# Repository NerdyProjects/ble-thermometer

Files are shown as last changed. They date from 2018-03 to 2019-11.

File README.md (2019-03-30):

# Bluetooth Low Energy Thermometer

This project describes a bluetooth low energy thermometer.

All code licenced as GPLv3, all documentation and PCB as CC0.

## Purpose
### Conceptual idea: fertility awareness method thermometer

The fertility awareness method, especially the symptothermal method, is a method to classify a woman's fertility by carefully monitoring symptoms of the body to be able to know in which state of the menstrual cycle she is.
One of the monitored symptoms is the body temperature:
The fundamental body temperature is normally taken early in the morning, directly after waking up after a restful sleep.
Women using this method, mostly use a clinical thermometer that has two digits, so a resolution of 0.01 °C.
To get an accurate measurement, measuring inside the vagina or the anus for at least 2 minutes is strongly recommended.
Because of practical reason, most chose to measure inside the vagina.

As a fan of natural birth control, I wanted to support woman by providing a device that relieves them of some stress of the temperature measurement as well as provides additional, maybe interesting data:
  * Not having to think about measuring the temperature in the morning
  * Not having to set an alarm for the same time (for some people the measurement time has a strong influence on the temperature, so you should always measure at a similar time)
  * Being able to detect factors that change your temperature more easily
  * Maybe even providing a better safety of the method by providing more data
  * Not having to immediately write down the measurement result

So the idea was born:
A thermometer, 
  * that can be inserted into the vagina
    * over night
    * the whole day
    * maybe even just in the early morning for some minutes
  * that records and stores the temperature
  * that can be read out using a smartphone or a computer
  * where there is high value on the ease of use as well as user privacy (no cloud service)
  * that does not hide the complexity of the symptothermal method (e.g. ONLY a thermometer, not a full birth control solution)

Initially, I wrote down more thoughts in a [design.md](design document) which is very far from how reality evolved.

I decided to go for the following system design:
  * Battery powered device powered by the ST SPBTLE-1S Bluetooth low Energy System-on-Chip application processor
  * Bosch BMP280 temperature/pressure sensor (because its high accuracy, low power usage, ease of use and my experience with it)
  * BR1632 lithium coin cell (because of availability as high temperature device)
  * altogether put on a small pcb surrounded by silicone to be completely safe to be used in contact with skin or mucous membrane

This design has a few limitations that are clear even before the first prototype has been built:
  * Limited battery lifetime: Device becomes unusable after ~1-3 years
    * Battery can be exchanged by replacing the silicone
  * High price: Pure materials cost ~15 € per piece
  * Silicone mould might need fiddling a bit

## Prototype
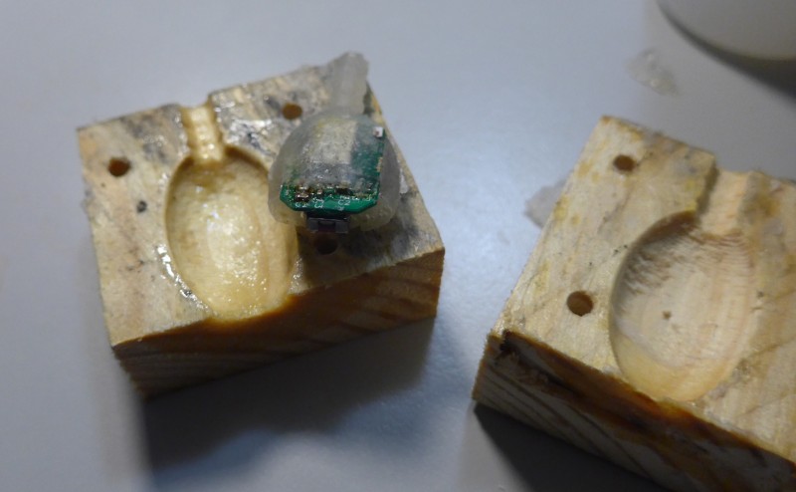
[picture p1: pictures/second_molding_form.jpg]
first mould form and a non-working prototype

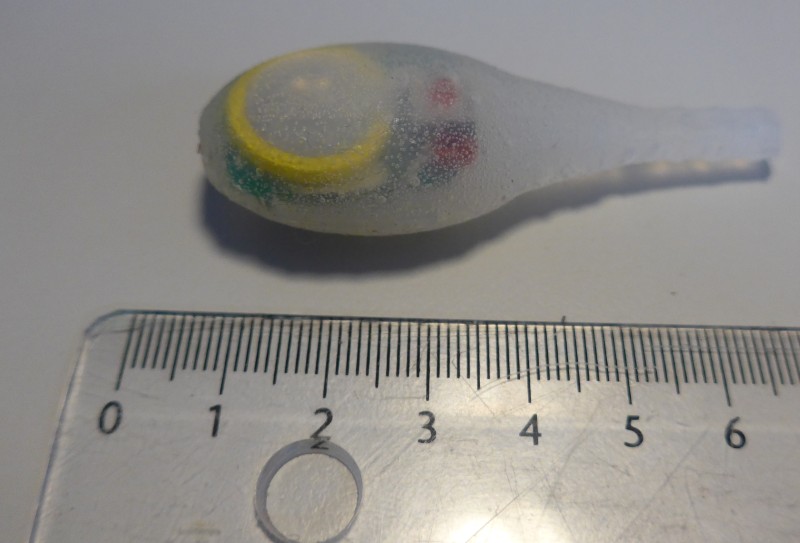
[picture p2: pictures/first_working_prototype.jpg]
first working prototype with refined form


## System architecture
The SPBTLE-1S is a System-on-Chip including a Cortex M0 processor, some flash and Ram, typical microcontroller peripherals and a bluetooth low energy radio.
The bluetooth low energy radio comes with a proprietary, binary-only library, that is linked to the custom user program and provides high level methods to configure the bluetooth part of the device as well as transfer data.

Different libraries are provided by ST that allow creating a running application easily.

The device contains two softwares:
  * The OTA Service Manager, which openly listens for bluetooth connections to reprogram the firmware. It is started after powerup and automatically boots the application software after some seconds.
  * The actual application software. It implements a "safety feature" Long pressing the button (for > 25 seconds) resets the chip, starting in the OTA Service Manager.

## Theory of operation
The thermometer device has different operating modes, whereby it should be kept in mind that the device itself can never be completely powered off.

  * Standby: Time-tracking mode, just counts how long in the past the last measurement has been taken. Can be woken up by button press.
  * Recording: The device takes a measurement point in a fixed (but configurable) interval. Up to 4096 points can be stored before the oldest one gets overwritten.
  * Connectable: The device advertises its Bluetooth low Energy services and is connectable by a paired device. As this mode takes quite some power, it should only be active for a short time.
  * Connected: The device is connected to another device. Data can be read out, configuration can be changed. This mode also takes a bit more power and should only be active for a short time.
  * Pairable: The device advertises its services and is connectable and pairable by other devices.

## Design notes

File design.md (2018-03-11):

# Description

This project describes a thermometer, that should be able to measure temperatures in intervals over a certain time span.
It should be small, self-powered, reusable and easy to be used.
Its designed purpose is especially for fertility awareness methods but also for general sports and medical purposes.
Therefore, it should fulfil the following criteria:

* Small in size to be inserted into the vagina for some period of time
  * Ideally, also swalloable if possible in size
* Safe to not impose any allergic potential
* rechargable battery life time of at least 24 hours
* Wirelessly rechargable
* Wireless data transfer
* storage capacity for a measurement every 5 minutes -> 720 temperature measurements from 25 .. 45 degrees with a resolution of 0.01 degree -> min. 12 kBit of storage space

# Design proposal

## NFC and energy harvesting

A simple design could use NFC and energy harvesting.
Available hardware components could be:

* M24LR16E 16 kBit NFC I2C EEPROM with energy harvesting (avalable in MSOP package); 30µA standby (or turn off); 5ms byte write @220µA; 2.0x3.0mm
* a 15mmx15mm PCB antenna 
* a BMP280 thermometer as small, energy efficient (~2µA average, down to 1.8V); LGA 2.0x2.5mm
* an AT Tiny 13A microcontroller (~4µA PowerDown/Watchdog; 40µA active @128 kHz); 3.0x3.0mm

### Power calculation
* EEPROM write: 0.0016 As for 720 writes
* EEPROM standby: 2.6 As for 24h standby (turn off!)
* Controller: 0.432 As for 24h power down, 0.015 As for 720 measurements
* BMP280: 0.2 As for 24h power down and measuring (or turn off as well for less)

Voltage min. 1.8V, charge 3.6V -> 1.8V difference; Q/Udiff=C; 0.5 As / 1.8V ~ 0.27As/V -> 0.33F cap would fulfill the criteria

Charge time: ~2-3 minutes (small cap), ~5-8 minutes (big cap)

### Mechanical Dimensions
PCB Antenna and Chips fit on a surface of ~15mmx20mm. The board would have a thickness of 1.6mm + components (~2.5mm total)
A 0.33F Goldcap would come as 11mm diameter, 5mm thickness
A 1F Goldcap would come as 20mm diameter, 6.5mm thickness

Antenna should be kept free from both sides, so cap needs to be on the side -> 15mm + (11/20mm) total length, 15/20mm total width, 7.5/9mm thickness

Also, it needs a silicon cover, maybe 2mm thickness all around?
* Small cap: 30mm length, 20mm width, 11.5mm thick
* Big cap: 40mm length, 24mm width, 13mm thick

## Bluetooth low energy and coin battery

Another solution could be using a coin button cell and an integrated bluetooth low energy module.
Available hardware components:

* SPBTLE-1S module (~10 years standby from a 100mAh coin battery (0.9µA); ~1.9mA active; includes 24kByte of retention sram; includes all of processor/antenna/etc.) 13.5x11.5mm
* BMP280 (sleep 0.3µA; active 325µA for ~2ms/measurement)
* small circuit board to connect battery/BMP280/SPBTLE-1S
* Coin battery CR1632
* Small button to activate BTLE by pressing the whole module together? (Not for current consumption reasons but maybe more "radiation" concerns of users)

### Power consideraton

* BTLE standby/advertising rarely: ~1 µA
* BMP280 sleep: ~0.3 µA
* BMP280 measuring every minute with 16x oversampling: ~0.2 µA
* BTLE data transfer every day of 12 kBit (round 1 s of active time per day at ~10mA): ~0.1 µA

Sum + rounding: ~2 µA
Battery lifetime: ~5 years with 100mAh battery

### Mechanical dimensions
* Module with antenna: 13.5x11.5mmx2.0mm
* board underneath 1.0mm
* board overstand/total size: 15mmx16mmx3mm
* battery CR1632 aside: 16mm diameter, 3.2mm height

* Battery aside including silicon: 35x20x7.2mm
* Battery below: 20x20x10.2mm

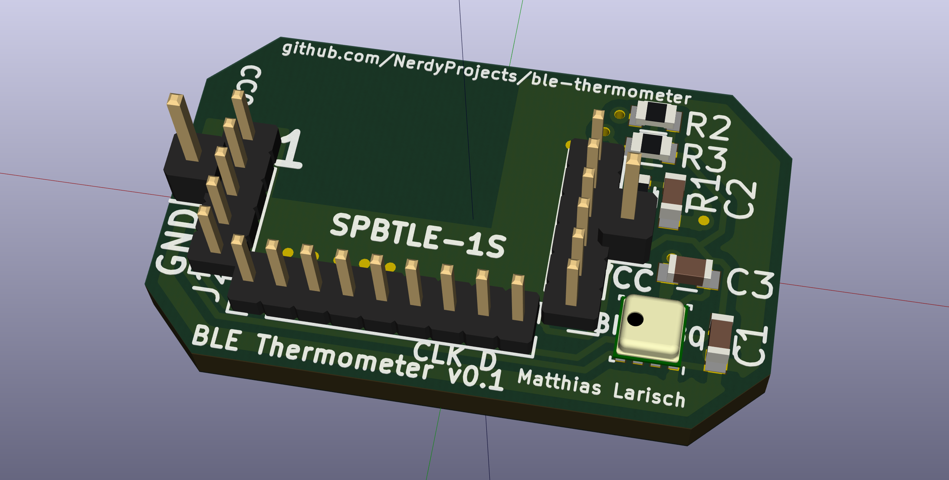
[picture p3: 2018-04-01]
pcb/ble.png

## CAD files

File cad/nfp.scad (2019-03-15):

length = 38;
width = 22;
height = 18;
//wood_cutout_for_connection = 8;
//connection_width = 4;
drill_width = 3;
module form() {
    resize([length,width,height]) minkowski() {
        resize([length,width,height]) sphere(1, $fn=30);
        sphere(3, $fn=15);
    }
    translate([-28,0,0]) rotate([0,90,0]) cylinder(r1=3.5,r2=8.3,h=20, $fn=50);
    
    translate([-50,0,0]) rotate([0,90,0]) cylinder(d=6,h=40, $fn=10);
    translate([-30,0,0]) rotate([0,90,0]) cylinder(d=7,h=2, $fn=10);
    translate([-25,0,0]) rotate([0,90,0]) cylinder(d=7,h=2, $fn=10);
    translate([-35,0,0]) rotate([0,90,0]) cylinder(d=7,h=2, $fn=10);
    translate([-40,0,0]) rotate([0,90,0]) cylinder(d=7,h=2, $fn=10);
    translate([-20,0,0]) rotate([0,90,0]) cylinder(d=7,h=2, $fn=10);
    translate([-45,0,0]) rotate([0,90,0]) cylinder(d=7,h=2, $fn=10);
    translate([-50,0,0]) rotate([0,90,0]) cylinder(d=7,h=2, $fn=10);
}

/*difference() {
    translate([-50, -15]) square([72,30]);
    translate([-45, -10]) circle(d=drill_width, $fn=50);
    translate([-45, 10]) circle(d=drill_width, $fn=50);
    translate([-18, -11]) circle(d=drill_width, $fn=50);
    translate([-18, 11]) circle(d=drill_width, $fn=50);
    translate([18, -11]) circle(d=drill_width, $fn=50);
    translate([18, 11]) circle(d=drill_width, $fn=50);
}
*/

translate([-11, 0, -9.5]) resize([7, 20, 5]) minkowski() {
    resize([10, 20, 5]) sphere(1, $fn=50);
}

difference() {
    translate([-50, -15, -24]) cube([72,30,24]);
    form();
    // finger placement for button
    // top cutout for filling/
    //translate([-12.5, -7.5, -43]) cube([25,15,40]);
    //translate([-20, -12, -50]) cylinder(d=4,h=100, $fn=10);
    //translate([-20, 12, -50]) cylinder(d=4,h=100, $fn=10);
    //translate([18, 12, -50]) cylinder(d=4,h=100, $fn=10);
    //translate([18, -12, -50]) cylinder(d=4,h=100, $fn=10);
    //translate([-45, 12, -50]) cylinder(d=4,h=100, $fn=10);
    //translate([-45, -12, -50]) cylinder(d=4,h=100, $fn=10);
}

//translate([10, 15, -15 - wood_cutout_for_connection]) cube([connection_width, 5, 15]);
//translate([-18, 15, -15 - wood_cutout_for_connection]) cube([connection_width, 5, 15]);
//translate([10, -20, -15 - wood_cutout_for_connection]) cube([connection_width, 5, 15]);
//translate([-18, -20, -15 - wood_cutout_for_connection]) cube([connection_width, 5, 15]);
//translate([22, -20, -15 - wood_cutout_for_connection]) cube([10, 40, 15]);
//translate([-63, -20, -15 - wood_cutout_for_connection]) cube([10, 40, 15]);
//rotate([180, 0, 0]) difference() {
//    translate([-35, -15, 0]) cube([60,30,3]);
//    form();
//}

// form();
 //color("grey") cube([25,14,7], center=true);

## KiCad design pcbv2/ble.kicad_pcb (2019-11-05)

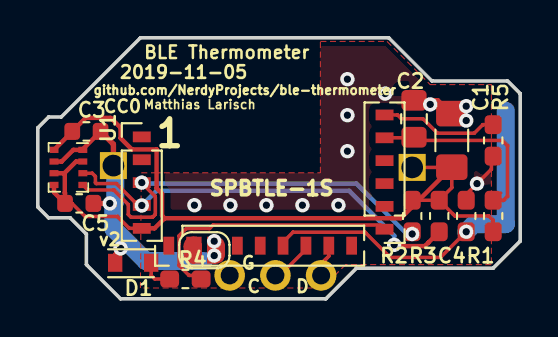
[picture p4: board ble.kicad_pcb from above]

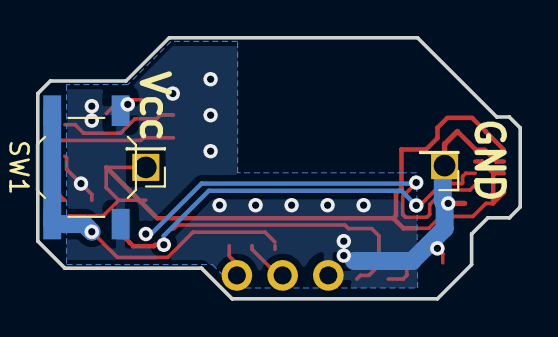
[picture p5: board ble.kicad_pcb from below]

Board: 2 copper layers, 26.8 x 14.5 mm, 20 parts (3 on the bottom side), 12 nets.

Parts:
C1: 100µ/6,3V; C_1206_3216Metric_Pad1.42x1.75mm_HandSolder
C2: 10µ; C_0805_2012Metric_Pad1.15x1.40mm_HandSolder
C3, C5: 100n; C_0603_1608Metric
C4: 100n; C_0603_1608Metric_Pad1.05x0.95mm_HandSolder
D1: VLMO20J2M1-GS08; LED_miniPLCC_2315
J1: Conn_01x05; PinHeader_1x05_P1.27mm_Vertical
J2: Conn_01x09; PinHeader_1x09_P1.27mm_Vertical
J3: Conn_01x06; PinHeader_1x06_P1.27mm_Vertical
J4: Conn_01x03; PinHeader_1x03_P2.54mm_Vertical
J5, J6: Conn_01x01; PinHeader_1x01_P2.00mm_Vertical
JP1: BOOT; SolderJumper-2_P1.3mm_Open_RoundedPad1.0x1.5mm
R1: 47k; R_0603_1608Metric_Pad1.05x0.95mm_HandSolder
R2, R3: 4k7; R_0603_1608Metric_Pad1.05x0.95mm_HandSolder
R4: 470; R_0603_1608Metric_Pad1.05x0.95mm_HandSolder
R5: 10k; R_0603_1608Metric_Pad1.05x0.95mm_HandSolder
SW1: SW_Push; SW_SPST_TL3342
U1: BMP280; Bosch_LGA-8_2x2.5mm_P0.65mm_ClockwisePinNumbering

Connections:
GND: C1.2, C2.2, C3.2, C4.2, C5.2, D1.1, J2.3, J4.3, J6.1, JP1.1, R5.1, SW1.2, U1.1, U1.7
unnamed: C4.1, J2.6, SW1.1
unnamed: D1.2, R4.1
unnamed: J2.2, JP1.2
unnamed: J3.1, R4.2
unnamed: J3.6, R5.2
RESET_N: C2.1, J3.5, R1.2
SCL: J1.3, R2.2, U1.4
SDA: J1.4, R3.2, U1.3
SWCLK: J2.7, J4.2
SWDIO: J2.8, J4.1
VCC: C1.1, C3.1, C5.1, J1.5, J5.1, R1.1, R2.1, R3.1, U1.2, U1.5, U1.6, U1.8

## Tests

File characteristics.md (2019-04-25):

# Prototype board v1

## Errata
### HW
  * BMP280 footprint too big (BME280)
  * BMP280 VccIO not connected (seems to be no big deal, CSP is connected to VCC, ESD diodes work well, IO does only need to pulldown, slow I2C possible
  * BR1632 does not like the discharge current so much. Install min. 100µF in parallel to the battery to lower the pulse stress a lot (0.1V for 1 ms @ 10 mA)
  * DIO12 should be pulled down for less current consumption
  * DIO7/boot should not be permanently connected to GND but via pulldown (to be able to change BOOT mode by pulling it up)
  * LED towards GND on DIO0
  * BMP should be further at the side of the pcb: complete design would allow bmp to stick out into the handle
  * Reset time constant must be increased a lot, e.g. 10µF or 470k
### SW
  * edaa4536 most recent measurement time is way too big sometimes

## Operating characteristics
  * Vcc >= 1.9 V stable, at ~1.75V it turned off. BMP seemed stable to the end.
  * Connection interval leads to ~1ms of oscillator startup at ~1.4 mA, then ~1ms of operation at 7 mA peak, ~5.8 mA average
  * BMP measurement wakeup takes ~3.5 ms at ~3 mA
  * BMP measurement seems to take ~17ms at ~450µA
  * Sending wakeup peaks at ~10mA, otherwise similar to connection interval
  * TI White Paper SWRA349 (http://www.ti.com/lit/wp/swra349/swra349.pdf) suggests a ~25µF capacitor to handle these peak loads better. This would require a 50ms connection interval to allow the battery to reload the capacitor when there is only idle current usage.
  * An overnight-result counting the time driven by VTimer had an error of ~120 seconds in ~10 hours. Acceptable, but quite big...
    * This might still be another problem as it was not reproducible looking at another hour of time in the morning (deviation of 0-2 seconds / hour which is significantly less)
  * Time constant for temperature change: device was put in cold water from stable 42 degrees. After 105 seconds, temperature was at 23.9 degrees (~1xtau), after 550 seconds at 13.05 degrees (which looks stabelized / water was heating up slowly afterwards)

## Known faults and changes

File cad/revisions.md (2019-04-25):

# 2019-03-20
  * length: 38mm
  * width: 22mm
  * height: 18mm
  * first button mark
  * first extension of handle for extended stability

## Visual feedback
  * The PCB is quite far in the front, also the silicone around the battery is really thin.
  * There is ~5mm of unused space in the back
  * There is ~5mm of unused space below the PCB.
  * Button mark ("hole") is too small. Positioning is not right but if PCB is a bit further back this would be solved
 
## User feedback
  * Do not use transparent silicone as it might be creepy to the user

## Improvement suggestions
  * decrease length by ~3mm
  * move PCB a bit further to the back: Make sure it sits exactly in the middle and put enough of the viscous silicone in the front
  * have the battery side on the bottom when molding. PCB should be just on top of the mold form e.g. only battery/switch/LED underneath, PCB will be inside the second half.
  * Put a ring around the base of the device (maybe getting rid of the handle or not) to avoid the device from falling out

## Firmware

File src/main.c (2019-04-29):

#include <stdio.h>
#include "BodyThermometer_config.h"
#include "BlueNRG1_it.h"
#include "BlueNRG1_conf.h"
#include "clock.h"
#include "osal.h"
#include "ble_const.h"
#include "bluenrg1_stack.h"
#include "sleep.h"
#include <string.h>
#include "gatt_server.h"
#include "sensor.h"
#include "app_flags.h"
#include "led.h"
#include "timer.h"
#include "adc.h"
#include "app.h"

#ifndef DEBUG
#define DEBUG 0
#endif

#if DEBUG
#define ASSERT_FALSE() while(1) { BlueNRG_Sleep(SLEEPMODE_CPU_HALT, 0, 0); }
#include <stdio.h>
#define PRINTF(...) printf(__VA_ARGS__)
#else
#define ASSERT_FALSE() NVIC_SystemReset()
#define PRINTF(...)
#endif



/** Set the watchdog reload interval in [s] = (WDT_LOAD + 3) / (clock frequency in Hz). */
#define RC32K_FREQ		32768
#define RELOAD_TIME(sec)        ((sec*RC32K_FREQ)-3)

#define LED_FLASH_ON_MS 20
#define LED_FLASH_OFF_MS 1500
#define LED_FAST_FLASH_ON_MS 20
#define LED_FAST_FLASH_OFF_MS 300
#define LED_BLINK_ON_MS 150
#define LED_BLINK_OFF_MS 400

#define SENSOR_READ_DURATION_MS 30
static volatile uint32_t sensor_update_rate = 15000;
/* recorder tracks time even when measurement is disabled. Notify time counter in this interval.
Interval is limited to 52xxxxx due to internal resolution/overflow.
Also, I had effects that look like overflows in the calculation, use less than half the allowed range
to work around any potential sign-issues. */
#define STANDBY_RECORDER_TIME_UPDATE_RATE 2600000
static uint32_t next_sensor_interval;

static volatile LedMode ledMode;
static volatile uint8_t ledState;
static volatile uint8_t ledCount;

volatile int app_flags;

void led_init(void) {
  GPIO_InitType gpio;
  /* Enable the GPIO Clock */
  SysCtrl_PeripheralClockCmd(CLOCK_PERIPH_GPIO, ENABLE);

  /* Configure LED as output */
  gpio.GPIO_Pin = GPIO_Pin_0;
  gpio.GPIO_Mode = GPIO_Output;
  gpio.GPIO_Pull = DISABLE;
  gpio.GPIO_HighPwr = DISABLE;
  GPIO_Init(&gpio);
}

static void led_set_ll(uint8_t state) {
  if(state) {
    GPIO_SetBits(GPIO_Pin_0);
    ledState = 1;
  } else {
    GPIO_ResetBits(GPIO_Pin_0);
    ledState = 0;
  }
}

static void led_handle(void) {
  uint32_t nextTime;
  if(ledState == 0) {
    switch(ledMode) {
      case LED_BLINK:
      nextTime = LED_BLINK_ON_MS;
      break;
      case LED_FLASH:
      nextTime = LED_FLASH_ON_MS;
      break;
      case LED_FAST_FLASH:
      nextTime = LED_FAST_FLASH_ON_MS;
      break;
      case LED_OFF:
      default:
      return;
    }
    led_set_ll(1);
    HAL_VTimerStart_ms(LED_TIMER, nextTime);
    if(ledCount) {
      if(--ledCount == 0) {
        ledMode = LED_OFF;
      }
    }
  } else {
     switch(ledMode) {
      case LED_BLINK:
      nextTime = LED_BLINK_OFF_MS;
      break;
      case LED_FLASH:
      nextTime = LED_FLASH_OFF_MS;
      break;
      case LED_FAST_FLASH:
      nextTime = LED_FAST_FLASH_OFF_MS;
      break;
      case LED_OFF:
      default:
      led_set_ll(0);
      return;
    }
    led_set_ll(0);
    HAL_VTimerStart_ms(LED_TIMER, nextTime);
  }
}

/* set LED mode. If count is non-zero, only play pattern count times. */
void led_set(LedMode mode, uint8_t count) {
  HAL_VTimer_Stop(LED_TIMER);
  ledMode = mode;
  ledCount = count;
  led_set_ll(0);
  led_handle();
}

#if DEBUG
static void uart_putc(uint8_t tx_data)
{
  while (UART_GetFlagStatus(UART_FLAG_TXFF) == SET);
  UART_SendData(tx_data);
}
#endif

void _debug(char *msg)
{
  #if DEBUG
  while(*msg) {
    uart_putc(*(msg++));
  }
  #endif
}

void _debug_int(uint32_t num)
{
  #if DEBUG
  char buf[8];
  buf[7] = 0;
  for(int i = 0; i < 7; ++i) {
    int j = (num >> 4*i) & 0x0F;
    if(j < 10) {
      buf[6-i] = '0' + j;
    } else {
      buf[6-i] = 'A' + j - 10;
    }
  }
  debug(buf);
  #endif
}

void _debug_uint8(uint8_t num)
{
  #if DEBUG
  char buf[3];
  buf[2] = 0;
  for(int i = 0; i < 2; ++i) {
    int j = (num >> 4*i) & 0x0F;
    if(j < 10) {
      buf[1-i] = '0' + j;
    } else {
      buf[1-i] = 'A' + j - 10;
    }
  }
  debug(buf);
  #endif
}

void uart_init(void)
{
  #if DEBUG
  UART_InitType UART_InitStructure;

  SysCtrl_PeripheralClockCmd(CLOCK_PERIPH_UART | CLOCK_PERIPH_GPIO, ENABLE);

  GPIO_InitType GPIO_InitStructure;

  GPIO_InitStructure.GPIO_Pin = GPIO_Pin_8;
  GPIO_InitStructure.GPIO_Mode = Serial1_Mode;
  GPIO_InitStructure.GPIO_Pull = DISABLE;
  GPIO_InitStructure.GPIO_HighPwr = DISABLE;
  GPIO_Init(&GPIO_InitStructure);

  UART_InitStructure.UART_BaudRate = 460800;
  UART_InitStructure.UART_WordLengthTransmit = UART_WordLength_8b;
  UART_InitStructure.UART_WordLengthReceive = UART_WordLength_8b;
  UART_InitStructure.UART_StopBits = UART_StopBits_1;
  UART_InitStructure.UART_Parity = UART_Parity_No;
  UART_InitStructure.UART_HardwareFlowControl = UART_HardwareFlowControl_None;
  UART_InitStructure.UART_Mode = UART_Mode_Tx;
  UART_InitStructure.UART_FifoEnable = ENABLE;
  UART_Init(&UART_InitStructure);

  UART_Cmd(ENABLE);
  #endif
}

static void button_init(void)
{
  GPIO_InitType gpio;
  /* Enable the GPIO Clock */
  SysCtrl_PeripheralClockCmd(CLOCK_PERIPH_GPIO, ENABLE);

  /* Configure BUTTON as interrupt sources */
  gpio.GPIO_Pin = GPIO_Pin_11;
  gpio.GPIO_Mode = GPIO_Input;
  gpio.GPIO_Pull = ENABLE;
  gpio.GPIO_HighPwr = DISABLE;
  GPIO_Init(&gpio);

  /* Set the GPIO interrupt priority and enable it */
  NVIC_InitType NVIC_InitStructure;
  NVIC_InitStructure.NVIC_IRQChannel = GPIO_IRQn;
  NVIC_InitStructure.NVIC_IRQChannelPreemptionPriority = LOW_PRIORITY;
  NVIC_InitStructure.NVIC_IRQChannelCmd = ENABLE;
  NVIC_Init(&NVIC_InitStructure);

  /* Configures EXTI line */
  GPIO_EXTIConfigType GPIO_EXTIStructure;
  GPIO_EXTIStructure.GPIO_Pin = GPIO_Pin_11;
  GPIO_EXTIStructure.GPIO_IrqSense = GPIO_IrqSense_Edge;
  GPIO_EXTIStructure.GPIO_Event = GPIO_Event_Both;
  GPIO_EXTIConfig(&GPIO_EXTIStructure);

  /* Clear pending interrupt */
  GPIO_ClearITPendingBit(GPIO_Pin_11);

  /* Enable the interrupt */
  GPIO_EXTICmd(GPIO_Pin_11, ENABLE);
}

/* called from button edge interrupt and when button wakeup source detected - detect situation inside.
   Care: We might be in interrupt context.
 */
void button_handle(void) {
  static uint32_t lastPressTime;
  static uint8_t lastState = Bit_SET;
  uint8_t state = GPIO_ReadBit(GPIO_Pin_11);
  /* The key handling is dependent on HAL timer (powered by systick timer). That should work also with sleep modes
  as the keys' state is also a wakeup source, so the time should be increasing while the button is pressed. */
  if(state != lastState) {
    uint32_t time = HAL_VTimerGetCurrentTime_sysT32();
    if(state == Bit_RESET) {
      lastPressTime = time;
    } else {
      int32_t pressDuration = HAL_VTimerDiff_ms_sysT32(time, lastPressTime);
      if(pressDuration > 25000) {
        NVIC_SystemReset();
      } else if(pressDuration > 6000) {
        /* activate bluetooth pairing */
        debug("PAIR\n");
        APP_FLAG_SET(SET_PUBLIC_CONNECTABLE);
      } else if(pressDuration > 1500) {
        if(APP_FLAG(MEASUREMENT_ENABLED)) {
          APP_FLAG_SET(REQUEST_DISABLE_RECORDING);
        } else {
          APP_FLAG_SET(REQUEST_ENABLE_RECORDING);
        }
      } else if(pressDuration > 300) {
        /* (de)activate bluetooth connection */
        if(APP_FLAG(CONNECTABLE) || APP_FLAG(CONNECTED)) {
          APP_FLAG_SET(REQUEST_DISABLE_BLE);
        } else {
          debug("CONN\n");
          APP_FLAG_SET(SET_DIRECTED_CONNECTABLE);
        }
      }
    }
    lastState = state;
  }
}


void enable_measurement(void)
{
  sensor_init();
  if(!APP_FLAG(SENSOR_UNAVAILABLE)) {
    next_sensor_interval = HAL_VTimerGetCurrentTime_sysT32();
    /* initially measure sensor now */
    APP_FLAG_SET(MEASUREMENT_ENABLED);
    HAL_VTimerStart_ms(SENSOR_TIMER, 100);
  }
}

static void APP_Init(void)
{
  led_init();
  recorder_ring_clear();
  Add_Services();
}


void disable_measurement(void)
{
  APP_FLAG_CLEAR(MEASUREMENT_ENABLED);
  APP_FLAG_CLEAR(SENSOR_MEASUREMENT_TRIGGERED);
  sensor_deinit();
  recorder_disable_recording();
}

void set_measurement_interval(uint16_t seconds)
{
  /* update recorder with measurement interval _previous_ to this update */
  recorder_set_recording_interval(get_measurement_interval());
  sensor_update_rate = seconds * 1000;
}

uint16_t get_measurement_interval(void)
{
  return sensor_update_rate / 1000;
}

static void trigger_sensor_measurement(void) {
  if(sensor_measure() != SENSOR_SUCCESS) {
    APP_FLAG_SET(SENSOR_UNAVAILABLE);
    debug("trigger sensor fail\n");
  } else {
    APP_FLAG_SET(SENSOR_MEASUREMENT_TRIGGERED);
    /* Use sensor timer for conversion timing. Do not alter sensor interval timing to be able to achieve constant period. */
    HAL_VTimerStart_ms(SENSOR_TIMER, SENSOR_READ_DURATION_MS);
  }
}

static void APP_Tick(void)
{
  if(APP_FLAG(REQUEST_DISABLE_RECORDING)) {
    APP_FLAG_CLEAR(REQUEST_DISABLE_RECORDING);
    disable_measurement();
    APP_FLAG_CLEAR(REQUEST_DISABLE_RECORDING);
    led_set(LED_FAST_FLASH, 2);
  }
  if(APP_FLAG(REQUEST_ENABLE_RECORDING)) {
    APP_FLAG_CLEAR(REQUEST_ENABLE_RECORDING);
    enable_measurement();
    recorder_enable_recording();
    led_set(LED_FAST_FLASH, 4);
  }
  if(!APP_FLAG(MEASUREMENT_ENABLED) && APP_FLAG(CONNECTED) && !APP_FLAG(MEASUREMENT_ENABLED)) {
    /* always measure while a connection is active */
    enable_measurement();
  }
  if(APP_FLAG(MEASUREMENT_ENABLED) && !APP_FLAG(CONNECTED) && !APP_FLAG(RECORDING_ENABLED)) {
    /* stop measurement again when disconnected and not recording */
    disable_measurement();
  }
  if(APP_FLAG(ADC_START_BATTERY_MEASUREMENT_TIME)) {
    APP_FLAG_CLEAR(ADC_START_BATTERY_MEASUREMENT_TIME);
    HAL_VTimerStart_ms(ADC_TIMER, BATTERY_MEASUREMENT_TIME);
  }
  if(APP_FLAG(SENSOR_TIMER_ELAPSED)) {
    APP_FLAG_CLEAR(SENSOR_TIMER_ELAPSED);
    if(APP_FLAG(MEASUREMENT_ENABLED) && !APP_FLAG(SENSOR_UNAVAILABLE)) {
      if(APP_FLAG(SENSOR_MEASUREMENT_TRIGGERED)) {
        APP_FLAG_CLEAR(SENSOR_MEASUREMENT_TRIGGERED);
        debug("S READ\n");
        int16_t temperature = sensor_read_temperature();
        SensorError res = sensor_get_error(0);
        if(res != SENSOR_SUCCESS) {
          debug("S ERR\n");
          /* This temperature result is invalid. Sensor code already reset hardware, but there is no result available at this point */
          if(res == SENSOR_ERROR_PERSISTENT) {
            debug("SENSOR UNVAILABLE\n");
            APP_FLAG_SET(SENSOR_UNAVAILABLE);
          }
          if(res == SENSOR_ERROR_TEMPORARY) {
            debug("retrigger sensor after error\n");
            trigger_sensor_measurement();
          }
        } else {
          Temp_Update(temperature, next_sensor_interval);
          /* step absolute sensor interval for constant period */
          next_sensor_interval = HAL_VTimerAcc_sysT32_ms(next_sensor_interval, sensor_update_rate);
          debug("sens int\n");
          HAL_VTimerStart_sysT32(SENSOR_TIMER, next_sensor_interval);
        }
      } else {
        trigger_sensor_measurement();
      }
    } else {
      Recorder_notify_time(next_sensor_interval);
      next_sensor_interval = HAL_VTimerAcc_sysT32_ms(next_sensor_interval, STANDBY_RECORDER_TIME_UPDATE_RATE);
      HAL_VTimerStart_sysT32(SENSOR_TIMER, next_sensor_interval);
    }
  }
  if(APP_FLAG(SENSOR_UNAVAILABLE)) {
    disable_measurement();
  }
  if(APP_FLAG(HANDLE_LED)) {
    APP_FLAG_CLEAR(HANDLE_LED);
    led_handle();
  }

}
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

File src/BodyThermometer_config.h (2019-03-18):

#ifndef _SENSORDEMO_CONFIG_H_
#define _SENSORDEMO_CONFIG_H_

#include "bluenrg1_stack.h"
#include "stack_user_cfg.h"
#include "OTA_btl.h"

/* This file contains all the information needed to init the BlueNRG-1 stack. 
 * These constants and variables are used from the BlueNRG-1 stack to reserve RAM and FLASH 
 * according the application requests
 */

/* Default number of link */
#define MIN_NUM_LINK            1
/* Default number of GAP and GATT services */
#define DEFAULT_NUM_GATT_SERVICES   2
/* Default number of GAP and GATT attributes */
#define DEFAULT_NUM_GATT_ATTRIBUTES 13

/* Enable/disable Data length extension Max supported ATT_MTU size based on OTA client & server Max ATT_MTU sizes capabilities */
#if (CONTROLLER_DATA_LENGTH_EXTENSION_ENABLED == 1) && (OTA_EXTENDED_PACKET_LEN == 1) 
  #define OTA_MAX_ATT_MTU_SIZE    (OTA_ATT_MTU_SIZE) //(220) /* OTA Client & Server supported ATT_MTU */   
#else /* BlueNRG-1 device: no data length extension support */
  #define OTA_MAX_ATT_MTU_SIZE    (DEFAULT_ATT_MTU)          /* DEFAULT_ATT_MTU size = 23 bytes */ 
#endif  

#if defined (ST_OTA_LOWER_APPLICATION) || defined (ST_OTA_HIGHER_APPLICATION)
/* Number of services requests from the Sensor demo */
#define NUM_APP_GATT_SERVICES (1 + 1) /* 2 Sensor services + 1 OTA service */

/* Number of attributes requests from the chat demo */
#define NUM_APP_GATT_ATTRIBUTES (7 + 9) /* 15 attributes x BLE Sensor demo services characteristics + 9 for OTA Service characteristics */

/**
 * Set the number of 16-bytes units used on an OTA FW data packet for matching OTA client MAX ATT_MTU
 */
#define OTA_16_BYTES_BLOCKS_NUMBER ((OTA_MAX_ATT_MTU_SIZE-4)/16)   /* 4 bytes for OTA sequence numbers + needs ack + checksum bytes */
   
/* OTA characteristics maximum lenght */
#define OTA_MAX_ATT_SIZE (4 + OTA_16_BYTES_BLOCKS_NUMBER * 16) 

#else /* NO OTA Service is required */

/* Number of services requests from the sensor demo */
#define NUM_APP_GATT_SERVICES 2

/* Number of attributes requests from the sensor demo */
#define NUM_APP_GATT_ATTRIBUTES 24

/* OTA characteristics maximum lenght */
#define OTA_MAX_ATT_SIZE (0) 
   
#endif

#define MAX_CHAR_LEN(a,b) ((a) > (b) )? (a) : (b)

/* Application characteristics maximum lenght */
#define _MAX_ATT_SIZE	(20) 

/* Set supported max value for attribute size: it is the biggest attribute size enabled by the application. */
#define APP_MAX_ATT_SIZE	  MAX_CHAR_LEN(OTA_MAX_ATT_SIZE,  _MAX_ATT_SIZE)

/* Number of links needed for the demo: 1
 * Only 1 the default
 */
#define NUM_LINKS               (MIN_NUM_LINK)

/* Number of GATT attributes needed for the sensor demo. */
#define NUM_GATT_ATTRIBUTES     (DEFAULT_NUM_GATT_ATTRIBUTES + NUM_APP_GATT_ATTRIBUTES)

/* Number of GATT services needed for the sensor demo. */
#define NUM_GATT_SERVICES       (DEFAULT_NUM_GATT_SERVICES + NUM_APP_GATT_SERVICES)

/* Array size for the attribute value for OTA service */
#if defined (ST_OTA_LOWER_APPLICATION) || defined (ST_OTA_HIGHER_APPLICATION)
/* OTA service: 4 characteristics (1 notify property): 99 bytes + 
   Image Content characteristic length = 4  + (OTA_16_BYTES_BLOCKS_NUMBER * 16); 4 for sequence number, checksum and needs acks bytes */
#define OTA_ATT_VALUE_ARRAY_SIZE (99 + (4 + (OTA_16_BYTES_BLOCKS_NUMBER * 16))) 
#else
#define OTA_ATT_VALUE_ARRAY_SIZE (0)       /* No OTA service is used */
#endif
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

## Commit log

2018-03-11 Design document and pcb v0.1
    [ble.kicad_pcb, ble.sch]
2018-03-12 Add github note
    [ble.kicad_pcb]
2018-04-01 Add pcb image
    [ble.kicad_pcb]
2019-02-06 3d model of second prototype
    [nfp.scad]
2019-02-08 Add drill holes
    [nfp.scad]
2019-02-10 Add screw holes to Cad model
    [nfp.scad]
2019-03-07 increase form size quite a bit
    [nfp.scad]
2019-03-12 optimized mill form
    [nfp.scad]
2019-03-12 serial debug, temperature history, button, battery
2019-03-12 prototype characteristics/errata
2019-03-15 decrease size, button marker, more stability
    [nfp.scad]
2019-03-18 Update pcb errata
2019-03-18 Implement temperature recording
2019-03-22 Fix sensor timer stopped on measurement stopped
2019-03-22 more power efficient LED patterns
2019-11-04 PCB v2
    [ble.kicad_pcb, ble.sch]
2019-11-05 Add second bme capacitor
    [ble.kicad_pcb, ble.sch]
